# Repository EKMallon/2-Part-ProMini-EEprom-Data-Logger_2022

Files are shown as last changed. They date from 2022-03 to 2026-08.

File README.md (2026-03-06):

banner image
# 2-Part-ProMini-EEprom-Data-Logger_2022

This program supports an ongoing series of DIY 'Classroom Logger' tutorials from Edward Mallon & Dr. Patricia Beddows at the Cave Pearl Project. The idea is to provide a starting point for student projects in environmental monitoring courses and/or thesis level research. In 2023 the logger base code was updated to match the newer the e360 model, being essentially identical except for the changes required for the alternate NTC and LED connections. <br/>
<br/>The tutorial that matches this code can be found at:<br/>
https://thecavepearlproject.org/2022/03/09/powering-a-promini-logger-for-one-year-on-a-coin-cell/
<br/>with a detailed building guide video at:<br/>
https://www.youtube.com/watch?v=58ps9fUyY0Q&t=0s&ab_channel=EdwardMallon

---
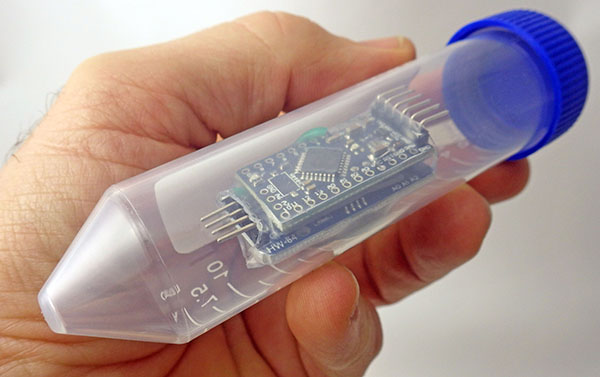
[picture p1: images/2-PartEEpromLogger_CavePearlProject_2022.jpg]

This 'low power' 2-module iteration runs the logger from a CR2032 coin cell and uses  EEprom memory to store sensor readings. This necessarily involves several power optimization steps which add significant complexity to the base code (as compared to previous versions) but hopefully everyone can read through the code and understand what is happening from the extensive comments. There are several manual configuration settings controlled by #define statements at the start of the program, and the logger will not be able to read the coincell voltage properly until you tweak the InternalReferenceConstant. <br/> <br/>
Data download & logger control are managed  through the IDE's serial monitor window at 500000 baud. 
The logger WILL NOT START taking readings until those serial handshakes are completed via the UART connection.<br/><br/>

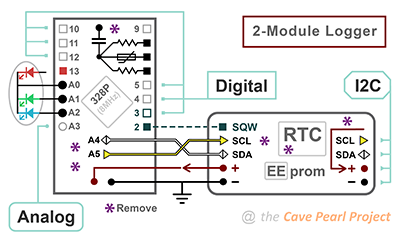
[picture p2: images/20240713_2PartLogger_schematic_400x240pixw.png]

The code has support for a built-in NTC / LDR combination, Bmp280, BH1750, and PIR sensors. These are enabled / disabled by uncommenting define statements at the beginning of the code. Each sensor enabled after the single-byte LowBat & RTCtemp defaults contributes two additional bytes per sampling event because every sensor reading gets stored in a 16-bit integer. The total bytes per saved per record must total 1, 2, 4, 8 or 16 only. Modifying the logger base code for a new type of sensor requires edits only at the areas indicated by call out numbers on the following flow charts. These are labeled with comments: STEP1, STEP2, STEP3, etc. so you can locate those sections with the Find function in the IDE.  They are surrounded by rows of ++PLUS++ symbols:</br>
>//++++++++++++++++++++++++++++++++++++++++++++++++++++</br>
>// STEP1 : #include libraries & Declare Variables HERE</br>
>//++++++++++++++++++++++++++++++++++++++++++++++++++++</br>
</br>


If all you do is enable the supported sensors via defines at the start of the program you won't have to deal with the low-level storage details.


 However to add new sensors you'll need to understand the I2C transaction that transfers those sensor readings into the EEprom at the end of the main loop. This involves dividing your sensor variables into 8-bit pieces and adding those bytes to the wire transfer buffer. This is accomplished with bit-math operations or via the lowByte & highByte macros.  The general pattern when sending bytes to an I2C EEprom is:</br>

```
Wire.beginTransmission(EEpromAddressonI2Cbus);
Wire.write(highByte(memoryAddress));
Wire.write(lowByte(memoryAddress));
loByte = lowByte(SensorReadingVariable); Wire.write(loByte);
hiByte = highByte(SensorReadingVariable); Wire.write(hiByte);
```

**add more Wire.write statements here as needed**  
You can ONLY add a total of 1, 2, 4, 8 or 16 DATA bytes to the I2C transaction. Powers of two increments are required because the recorded data must align with page boundaries inside the EEprom.

```
Wire.endTransmission();
```

The key insight here is that the wire library is only loading a memory buffer until Wire.endTransmission() is called. So it does not matter how much time you spend doing calculations, or slicing the variables, so long as you don't try and start another I2C transaction while you are still in the middle of this one. Once that buffer is physically sent over the wires, the EEprom enters a self-timed writing sequence and the logger reads the rail voltage while the CR2032 is under load. </br>

The data download function in setup retrieves those separate bytes and concatenates them back into the original integers - so the sequence of operations in the sendData2Serial function -STEP6- must exactly mirror the byte-order used to load the EEprom in the main loop.

---

Note: This script will still run on the older 3-module "Modules & Jumper Wires"  loggers described in the original Sensors paper: http://www.mdpi.com/1424-8220/18/2/530 
and provides a 'no SD card' operation on the older 2020 classroom logger described at https://thecavepearlproject.org/2020/10/22/pro-mini-classroom-datalogger-2020-update/ but you will have to change the LED pins. Sensor support and STARTUP MENU OPTIONS WILL CHANGE as the code evolves over time.

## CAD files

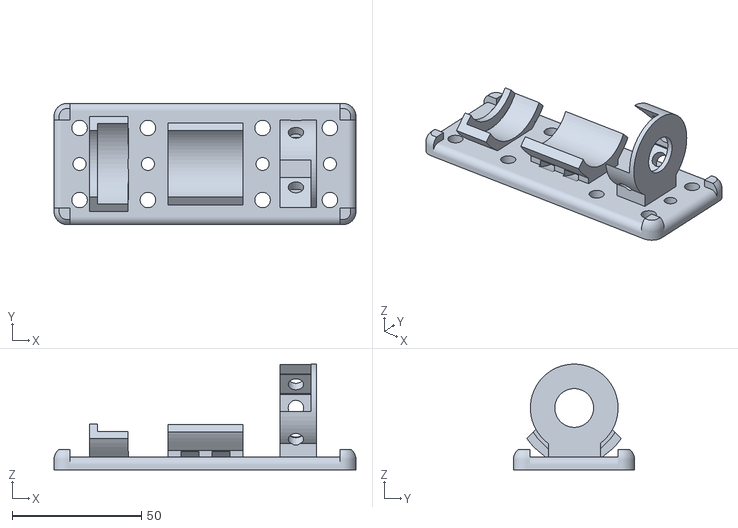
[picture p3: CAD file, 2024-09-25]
2PartLoggerr_30mlMountingBracket_v9_byEM_240923.stl
117.0 x 47.0 x 41.0

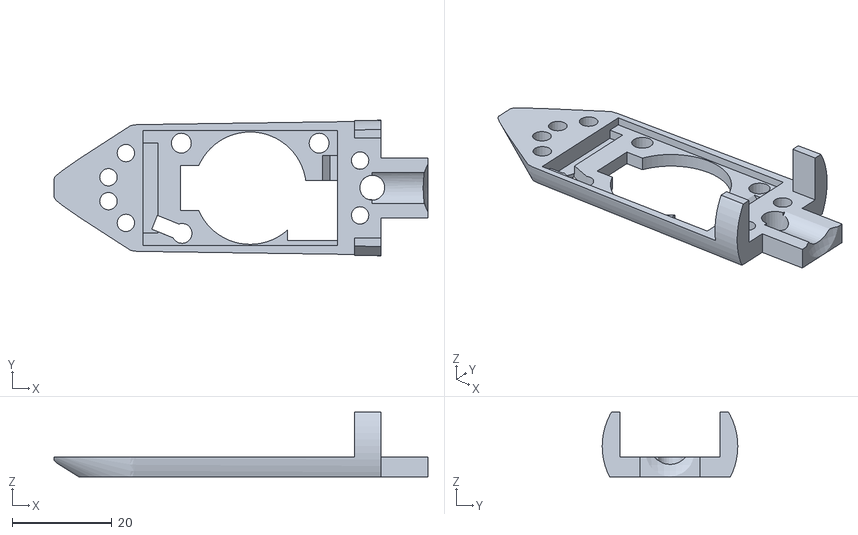
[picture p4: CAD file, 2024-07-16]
2PartProMiniLoggerRail.stl
75.1 x 27.2 x 13.0

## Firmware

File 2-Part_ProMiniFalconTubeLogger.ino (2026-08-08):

// 2-Part logger code by Edward Mallon - modified 2023 for e360 course at Northwestern University
// https://thecavepearlproject.org/2022/03/09/powering-a-promini-logger-for-one-year-on-a-coin-cell/
/*
This program supports an ongoing series of DIY 'Classroom Logger' tutorials from the Cave Pearl Project. 
The goal is to provide a starting point for self-built student projects in environmental monitoring.
This low power 2-module iteration runs from a CR2032 coin cell and uses EEprom memory to store sensor readings. 
Data download & logger control are managed through the IDE's serial monitor window at 500000 baud. 
The logger WILL NOT START until those serial handshakes are completed via a UART connection.
The most important rule to follow when adding new sensors is that this code can only accept 1, 2, 4, 8 or 16 sensorBytesPerRecord.
These 'powers of 2' fit in the I2C buffer AND divide evenly into the EEproms hardware page size to prevent page wrap-arounds.

The only library you MUST INSTALL for the minimum configuration of Promini & RTC module is LowPower [by LowPowerLab]
--------------------------------------------------------------------------------------------------------------------
this can be INSTALLED via the Library Manager or from https://github.com/LowPowerLab/LowPower

The following sensors require library installations before they can be used:
---------------------------------------------------------------------------
  BH1750 LUX sensor uses hp_BH1750  [by Stefan Armborst] via Lib Manager OR from https://github.com/Starmbi/hp_BH1750

  Sht30 Humidity sensor uses SHT85  [by Rob Tillaart] via Lib Manager OR from https://github.com/RobTillaart/SHT85/tree/master

  BMP280 uses BMP280_DEV  [by Martin Lindupp] which is available through the Lib Manager although the repo seems to have disappeared from github(?)

  BME280 (includes RH%) uses forcedBMX280  [by soylentOrange] which is available through the Lib Manager
  OR from https://github.com/soylentOrange/Forced-BMX280/tree/master NOTE that this library also works with the BMP280
  if you enable only recordBMEtemp_2byteInt and/or recordBMEpressure_2byteInt

*/

//++++++++++++++++++++++++++++++++++++++++++++++++++++++++++++++++++++++++++++++++   
//++++++++++++++++++++++++++++++++++++++++++++++++++++++++++++++++++++++++++++++++
// CURRENT 328p internal eeprom memory locations in use for start-up information
//++++++++++++++++++++++++++++++++++++++++++++++++++++++++++++++++++++++++++++++++   
//++++++++++++++++++++++++++++++++++++++++++++++++++++++++++++++++++++++++++++++++
/*
(0-3)     logger START TIME in unixtime (for reconstructiong timestamps later in sendSerial)
(4)       SampleIntervalMinutes
(5)       SampleIntervalSeconds
(6-9)     InternalReferenceConstant for calc. rail voltage from ADC in readRailVoltage
(10)      RTCagingOffset [adjusting by 3 compensates for ~ 1second of drift per month]
(12-15)   4byte UNIXtime of last time RTC was set by startMenu_setRTCtime - for drift tracking
(20-23)   NOT USED (yet) Sensor starting paramaters usually stored from (24) onwards

FOUR 100-CHARACTER 'text' info fields get stored in 328p internal eeprom:
Logger info:            64 to 164
Deployment info:        165 to 265
Calibration constants:  266 to 366
Site info:              367 to 467

These are output to screen by void setup_sendboilerplate2serialMonitor() when logger starts up
BUT you can store 'any' text in these fields, notes to self, normalization constants, etc
Note: we still have upper 512 bytes of 328p 1k eeprom availible for OLED screen fonts, etc.
// https://thecavepearlproject.org/2020/11/15/adding-two-oled-displays-to-your-arduino-logger-with-no-library/
*/

//++++++++++++++++++++++++++++++++++++++++++++++++++++++++++++++++++++++++++++++++   
//++++++++++++++++++++++++++++++++++++++++++++++++++++++++++++++++++++++++++++++++
// STEP0 :
// Create SENSOR definitions HERE to match the sensors you added to the logger
// Use these as global controls to enable/disable sensor code with #ifdef & #endif

// POWERS OF TWO rule: sensorBytesPerRecord for the enabled sensor combination MUST TOTAL 1,2,4,8 or 16
// IF you see a repeating error at download time it's probably because you violated that rule

//++++++++++++++++++++++++++++++++++++++++++++++++++++++++++++++++++++++++++++++++   
//++++++++++++++++++++++++++++++++++++++++++++++++++++++++++++++++++++++++++++++++

// LowestBattery & RTC_Temperature are the 2 byte 'base values' which are usually recorded with every sensor reading (as they require no extra sensor hardware beyond the logger itself)
#define logLowestBattery_1byte           // 1-byte (compressed): saves LowestBattery voltage recorded during EEprom saves
#define logRTC_Temperature_1byte         // 1-byte: the RTC's internal 0.25°C resolution temperature sensor

//Pressure sensor:
//#define readBMP280_Temp_2byte            // 2-bytes  // IF you enable all three BMP or BME outputs
//#define readBMP280_Pressure_2byte        // 2-bytes  // you will need two more bytes for an 8-byte record: try adding logLowestBattery_1byte & logRTC_Temperature_1byte 
//#define recordBMP280_Altitude_2byte      // 2-bytes: calculated by library


//#define readD7resistorwD6ref_2byte       // NTC? 2-bytes: ohms // for explanation of the method for reading analog resistance with digital pins see
//#define readD9resistorwD6ref_2byte       // LDR? 2-bytes: ohms // https://thecavepearlproject.org/2019/03/25/using-arduinos-input-capture-unit-for-high-resolution-sensor-readings/
                                           // 2022 note: 10k refference resistor on D6, NTC on D7, 300Ω on D8, LDR on D9 - does not match newer 2023 e360 NTC connections
                                         
//Light/Lux sensor:
//#define readBh1750_LUX_2byte             // 2-bytes: NOTE: raw sensor output gets converted to Lux during download

#define logCurrentBattery_2byte          // RARELY USED - not 1byte compressed like LowestBattery, primarily included as a powers-of-2 balancing option
//#define logFreeVariableMemory_2byte      // RARELY USED - primarily included as a powers-of-2 rule balancing option that does not rely on any external sensors

//#define readSi7051_Temp_2byte            // 2-bytes: used for NTC calibration - does not require a library, functions for si7051 at end of program

//#define readSht3x_Temp_2byte             // 2-bytes
//#define readSht3x_Humidity_2byte         // 2-bytes

#define recordBMEtemp_2byteInt           // 2-byte NOTE: works with both BMP & BME
#define recordBMEpressure_2byteInt       // 2-byte NOTE: works with both BMP & BME
//#define recordBMEhumidity_2byteInt       // 2-byte ONLY if BME 280 connected!

// AM312 Infrared Motion sensor:           // typically adds 10-15uA to sleep current //PIR drives its output line HIGH when it detects motion
//#define PIRcountPerInterval_2byte        // 2-bytes:  PIR is just an interrupt generating sensor, saves # of PIR HIGH events in a specified sample interval. Do not enable this with PIRtriggersReadings_4byte - choose one or the other
//#define PIRtriggersReadings_4byte        // 4-bytes for full Unix Timestamp every pass: Do not enable this with PIRcountPerInterval_2byte - choose one or the other
// PIR readme:
// PIRtriggers DOES NOT use the regular RTC-alarm based sampling interval but instead records the seconds elapsed between EVERY PIR trigger event in a uint32_t long variable [NOTE uint16_t overflows if no triggers within ~18 hours so change variable if you want longer intervals]
// PIRtriggersReadings_4byte usually enabled with four other bytes of sensor data [for a total of 8 bytes per record] OR with another 12 bytes of sensor data for a total of 16 bytes per record.
// AM312 has a hold time of about 2.0-2.3 sec and a blocking (cooldown) time of about 2 seconds, sensor STAYS HIGH indefinately if a new triggers occur when it is already high
// WARNING this can use alot of memory very quickly if PIR is triggered frequently!  - recommend use with larger eeprom memory attached

// TTP223 Capacitive Touch Switch:        // can be configured with jumpers for simmilar behavior to the AM312 - although the PIR has much longer (2s) signal HOLD-UP time
//#define TTP223countPerInterval_2byte    // 2-bytes: TTP223 is another interrupt generating sensor, saves #of Touch switch HIGH events in the start menu specified sample interval. Do not enable this WITH TTP233 triggersReadings_4byte - choose one mode  or the other
//#define TTP223triggersReadings_4byte    // Do not enable this with TTP223countPerInterval_2byte - choose ONE OR THE OTHER: saves 4-bytes Unix Timestamp every record so uses memory quickly
// TTP223 readme:                         // Like the PIR, TTP223triggers DOES NOT use the regular RTC-alarm sampling interval
// "Momentary" is typically the default for these modules with BOTH A AND B terminals left OPEN. For config info see: https://diyusthad.com/2019/06/how-to-use-ttp223-based-touch-switch.html
// With A&B open the output signal changes from (LOW) to state (HIGH) when a touch is detected and should return to (LOW) state when released
// SECURE THE TOUCH sensor WITH DROPS OF HOT GLUE on the side to avoid shaking the fragile breadboard connections!
// ALSO: trim down the header pins poking above the sensor surface board and cover them with conformal - if your finger touches the metal pins the touch will not register
// It may help to solder a small bypass cap directly onto the sensor module to stabilize power connections
// SLOW SENSOR RESPONSE TIME: ~220ms at VDD = 3V, Power-On Stabilization takes 0.5 seconds - Do not touch the pad during startup.
// The TTP223/TTP233 performs periodic auto-calibration. If environmental capacitance shifts during touch, the internal timer recalibrates the baseline after roughly 4 seconds.
// TTP233s do this after EVERY touch. If your finger is on the pad during the recalibration it may cause weird behavior or invert the response!
// Capactive sensors are sensitive to nearby interference: see https://forum.arduino.cc/t/ttp223-touch-sensors-self-triggering-bug/414967

//#define OLED_64x32_SSD1306               // not a sensor, but enabled with define to include needed library - requires 1000uF rail cap to smooth noise from 1306 charge pump!

// Default EEprom: 0x57 & 4096 here saves data into the 4k eeprom on the RTC module:
#define EEpromI2Caddr 0x57                    // Run a bus scanner to check where your eeproms are https://github.com/RobTillaart/MultiSpeedI2CScanner
#define totalBytesOfStorage 4096              // Default: 0x57 / 4096bytes to use the 4k eeprom on the RTC module 

// If saving to an external 32k I2C EEprom module: 
//#define EEpromI2Caddr 0x50                  // Run a bus scanner to check where your eeproms are https://github.com/RobTillaart/MultiSpeedI2CScanner
//#define totalBytesOfStorage 32768           // Default: 0x57 / 4096bytes to use the 4k eeprom on the RTC module 

// the Red LED on D13 gets used if BOTH of the following LED #define statements are commented out
#define LED_r9_b10_g11_gnd12               // enables code for RGB indicator LED // expects a 1k limit resistor on shared GND!
//#define LED_GndGB_A0_A2                  // For 2022 2-module build with NO breadboards: red channel leg on led cut, A0gnd Green A1, blue A2, default Red on d13 left in place

#include <Wire.h>       // I2C bus coms library: RTC, EEprom & Sensors
#include <EEPROM.h>     // note: requires default promini bootloader (ie NOT optiboot)
#include <avr/power.h>  // library for shutting down 328p chip peripherals to lower runtime current
#include <avr/sleep.h>  // provides SLEEP_MODE_ADC to lower current during ADC readings in readRailVoltage() function
#include <LowPower.h>   // this library NEEDS TO BE INSTALLED via the LIBRARY MANAGER for interval & battery recovery sleeps
                        // OR can be downloaded from LowPowerLab's repo (https://github.com/LowPowerLab/LowPower)
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

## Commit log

2022-03-10 remove duplication of RTC temp record
    RTC temp no longer saved with battery in OPD record with RTC_ONLY sensor configuration as this was redundant.
2022-03-10 bugfix: sendOPDreadings2Serial
    used #ifdef #else
    where criterion should have been:
    if (BatteryReadingEveryCycle){
2022-03-11 resistanceofCDScell set to uint32_t
    -to avoid overflow at night when values get very large
2022-03-11 set BatteryReadingEveryCycle = false;
    To once per day battery reading default value.
2022-03-12 Changed calculation for startup sync-delay
    At hour rollover, starts after one SampleIntervalMinutes
2022-03-14 Added comment
    NOTE: the current implementation of BatteryReadingEveryCycle doubles memory usage even though battery readings only happen 1/16 as often as sensor reads
    I will be posting a fix for this issue after the run tests underway now prove out.
2022-03-15 Many small tweaks throughout to remove duplicate battery reading save(s) when BatteryReadingEveryCycle = true; is set
    Required sensor data & opd data to use different calculations when reconstructing opd timestamp. Also required disable of normal midnightRollover=true; on clock rollover
2022-04-05 Multiple changes to OPD eeprom memory alignments
    -sensor data save moved to end of main loop
    -added if (LowestBattery <= systemShutdownVoltage){error;}
    -oncePerDayEvents now triggered by if (newBatteryReading)
    -Write_i2c_eeprom_array uses only if (newBatteryReading)
    -incrementing variables changed to uint32_t to prevent overflow with 64k
2022-11-13 Creating a buffer of 'zeros' in eerom between two data streams for readback stopcode
    if (forwardEEmemPointr > opdEEprMemPointer){break;}
    changed to
    if ((forwardEEmemPointr + sizeof(sensorDataBuffer)) >= opdEEprMemPointer){break;}
2023-02-24 Write_i2c_eeprom_array: relationship is INVERSE w 1.1v internal ref trick
    while (integerBuffer<OLDadcReading);
    changed to:
    while (integerBuffer>=OLDadcReading);
2023-04-30 ANNUAL global UPDATE
    This code supersedes all previous versions. MANY changes too numerous to itemize.
    Most notable ones being: ICU based sensor readings are now atomic. Deployment description input via serial.
    Sampling Intervals now input via serial with [hidden] support for SampleIntervalSeconds to allow rapid testing.
    New ADC looping method to capture lowest battery reading in Write_i2c_eeprom_array. Both High & Low battery recorded in OPD.
2023-05-05 Added LogCurrentBattery to option for sensor array readings
    a second single byte option allows the addition of the 1-byte RTC temp to LDR, etc without causing the 'powers of 2' violation for sensor array.
2023-05-22 Highest battery reset now occurs every OPD save
    HighestBattery = 0; // forces reset @ next readbattery
    midnight rollover now resets only LowestBattery
2023-05-22 Hi/Lo battery reset every OPD buffer load
    fixes update issue when saveeverycycle=true
2023-06-01 REMOVED system clock change to 1MHz in Write_i2c_eeprom_array
    Came across several cheap eBay eeproms that would freeze the system completely if the main cpu clock was changed while they were writing data. So I've removed that power saving technique from Write_i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
    Also added support for si7051 sensor to match photos shown in the blog.
2023-06-21 Minor bugfix to port settings in LDR & NTC readings
    added:
    DDRB &= B11111100; PORTB &= B11111100; //D9[LDR] & D8[300Ω] to INPUT(0) & LOW(0)
    DDRD &= B00111111; PORTD &= B00111111; //D7[NTC] & D6 [ref] to INPUT(0) & LOW(0)
2023-08-20 Update Write_i2c_eeprom_array function
    Larger EEproms require T0 & I2C peripherals to remain active in IDLE mode or they will occasionally hang while actively writing data. So sleep mode idle used after the I2C transfer. The default 4K ee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
2023-10-13 Simplified version: 2-Part_ProMiniFalconTubeLogger.ino
    Newer, low memory codebase for instrumentation course students at N.U. Removed the confusing buffer arrays & pointers - now saves bytes from sensor variables to 4K EEprom on RTC module at every pass 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
2023-10-25 Update README.md
    Code revisions are *currently underway* addendum
2023-10-25 removed #define LED_r9_b10_g11_gnd12
    Blog post uses different LED connections than the student lab version
2023-10-25 Bytes per record coment
    must be 1, 2,4,8,16 bytes (ie powers of 2) because of EEprom page boundaries
2023-12-01 Update 2-Part_ProMiniFalconTubeLogger.ino
    The students finally progressed through their courses far enough that I can release the complete code. Note that I've removed the complicated arrays as it turned out the power savings those buffers p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
2023-12-02 Update 2-Part_ProMiniFalconTubeLogger.ino
    changed SampleIntervals to uint8_t
2023-12-18 Fix ADC setting in LowPower.powerDown(SLEEP_FOREVER
    sleep&wait functions should use LowPower.powerDown(SLEEP_FOREVER, ADC_OFF, BOD_OFF);
    If the ADC somehow stays on you will get sleep currents of about 200uA
2024-01-09 void startMenu_setSampleInterval
    byteBuffer2 = SampleIntervalSeconds ? 60 % SampleIntervalSeconds : 0;
2024-02-29 ADC_OFF set to default during low power sleeps
    LowPower.powerDown(SLEEP_15MS, ADC_ON, BOD_OFF);
    LowPower.powerDown(SLEEP_15MS, ADC_OFF, BOD_OFF);
    in all areas except where ADC is being used
    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
2024-03-08 Update 2-Part_ProMinremoved power_all_disable(); from void error_shutdown()iFalconTubeLogger.ino
    as it was triggering high drain state on entering LowPower.powerDown(SLEEP_FOREVER
2024-04-09 ADC looping during EEsave & multiple changes to void error_shutdown()
    Looping the ADC reads with polling of the eeprom does a better job of catching the lowest point in the rail voltage during EEsave.
2024-04-16 Remove ADC loops during EEsave
    Any rail voltage fluctuations during EEsave can cause chip to hang. This is very hard to debug. Now just two ADC readings and low power idle sleep for duration of save.
2024-06-26 Update 2-Part_ProMiniFalconTubeLogger.ino
    added if(loByte<1){loByte=1;} check to NTC for calibration with no battery readings
2024-06-28 Update 2-Part_ProMiniFalconTubeLogger.ino
    Minor update conforming names on initial sensor defines.
2024-07-14 Update README.md
    Add flow charts
2024-07-16 Add files via upload
    3D printable rails for 30ml self standing centrifuge tube housings.
    [2PartProMiniLoggerRail.stl]
2024-09-16 Update 2-Part_ProMiniFalconTubeLogger.ino
    Indicator LED control moved to separate functions (see end of code) Using port commands. Note LED channels lit with internal PULLUP resistors to limit current load on the coincell.
2024-09-25 Add Logger Mounting Bracket to repo
    A logger mounting bracket for the 30ml housing tubes.
    [2PartLoggerr_30mlMountingBracket_v9_byEM_240923.stl]
2025-03-28 Update 2-Part_ProMiniFalconTubeLogger.ino
    ADDED Normalization Constants field and startMenu_updateLoggerInfoField is now unified function for all description info, ADDED support for sht3x sensors
2025-08-02 Update 2-Part_ProMiniFalconTubeLogger.ino
    Multiple small Updates: added logFreeVariableMemory_2byte for powers of two balancing option. ADDED void turnOnRedLED() which controls the D13 red on A2/3 LED configuration. readBattery() bugfix adde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
2026-01-05 Update 2-Part_ProMiniFalconTubeLogger.ino
    Removed parameter backup to simplify teaching codebuild. SERIAL On / Off moved to runtime options. Bugfix: LED routines for LED_r9_b10_g11_gnd12 failing to enable ground. Site info & Calibration info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
2026-01-13 Update 2-Part_ProMiniFalconTubeLogger.ino
    Changed pin states in initial Setup();
2026-03-06 BugFix
    Mistakenly had the e360 defs for resistor readings at the start of the 2-part code. Dhould have been: readD7resistorwD6ref_2byte & readD9resistorwD6ref_2byte. NTC reading in 2-part build uses 10k ref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

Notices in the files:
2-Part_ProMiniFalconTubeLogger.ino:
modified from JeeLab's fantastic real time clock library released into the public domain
